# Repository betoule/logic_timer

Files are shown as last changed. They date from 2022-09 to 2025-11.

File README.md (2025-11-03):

# Arduino Code to record precise TTL pulse timing for several lines in parallel over long duration

The provided code monitors TTL lines and put a 32 bit timestamp each
time a front is detected on one of the lines. The 32 bit timestamps,
provides more than 2000 seconds of monitoring with 0.5μs resolution,
and is provided by the microcontroller internal clock. A one byte flag
identifies the TTL line corresponding to each event.

The code is written for Atmega 2560 (monitoring up to 6 lines in
parallel) and 326P (up to 2 lines) and has been tested on Arduino Mega
2560 and Arduino Nano boards. The Arduino API being bypassed in
several places to solve performance and timing issues, port to other
microcontrollers may require a bit of work.

## Installation

The code comes in two parts: a firmware for the microcontroller unit
(MCU) and a python API handling the custom communication with the
MCU. Both live in the same repository than can be retrieve from github
with:

```
git clone https://github.com/betoule/logic_timer
```

### MCU code

The MCU code no longer requires the Arduino IDE. It can be compiled
and flashed using the regular avr suite.

+ Install everything needed with:
```
sudo apt install gcc-avr avr-libc avrdude make
```

+ Adjust the port and PORT, MCU, BAUD and PROGRAMMER entries in the
Makefile according to your board. The two supported chips are the
atmega328P and the mega2560 (default).

+ Connect the board, compile and upload the firmware with:
```
make
make flash
```

### Python API

Installation of the python API using pip is obtained as:

```
pip install .
```

## Usage

Connect the TTL and ground lines to the corresponding external
interrupt pins and ground pins on the Arduino board. The
correspondence between line identifiers and board pins is given for
the two implemented boards in the following table:

| Line Id | Flag   | Interrupt 2560 | Arduino Mega pin | Interrupt 326P | Arduino Nano pin |
|---------|--------|----------------|------------------|----------------|------------------|
| 0       | 1 << 0 | INT4           | 2                | INT0           | D2               |
| 1       | 1 << 1 | INT5           | 3                | INT1           | D3               |
| 2       | 1 << 2 | INT3           | 18               |                |                  |
| 3       | 1 << 3 | INT0           | 21               |                |                  |
| 4       | 1 << 4 | INT1           | 20               |                |                  |
| 5       | 1 << 5 | INT2           | 19               |                |                  |

The following picture displays a 3 lines implementation using an
Arduino Mega.
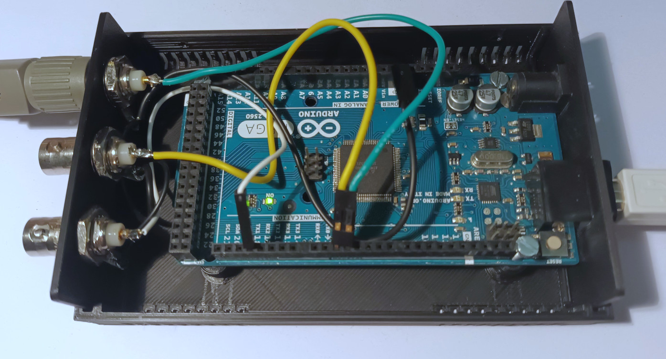
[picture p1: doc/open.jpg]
Lid open


STL files for the box are available in the 3D\_printed\_box
directory. Custom enclosure can easily been obtained with the
[ultimate box maker](https://www.thingiverse.com/thing:1264391).

Assuming that the path to the serial device corresponding to the
arduino is /dev/ttyACM0, the following command will trigger a 20 second
record of the rising edges of pin 2 and 3 and of the falling edge
of pin 18 and store the result to timing.npy: 

```
logic-timer -t /dev/ttyACM0 -d 20 -l 0r 1r 2f -o timing.npy
```

The result is a numpy record array with one entry for each detected
front and two columns *time* and *pinstate*. The timestamp in column
*time* is a 32 bit integer counting since the start of the record with
a resolution of 0.5μs. The 8 bit flag in column *pinstate* indicates
which line triggered the record according to the correspondence table
above. The record ends with a special entry whose *pinstate* value is
255. The corresponding timestamp gives the exact duration of the
monitoring.

As an example, the code below analyses a 20s record with a 1kHz square
wave in input 1. The plot displays the measured interval between
successive pulses. The rms of the measurements is 0.16 μs and peak to
peak deviation is 6 μs (see section Limitations for a discussion on
the timing accuracy).

```python
import numpy as np
import matplotlib.pyplot as plt
record = np.load('timing.npy')
t = record['time'][record['pinstate'] == 2]
t = t * 0.5e-6 # Convert timing in seconds
plt.plot(t[1:] - t[:-1], 'o')
plt.ylabel('Measured interval [s]')
plt.xlabel('Pulse number')
plt.tight_layout()
plt.savefig('doc/interval_accuracy.png')
```
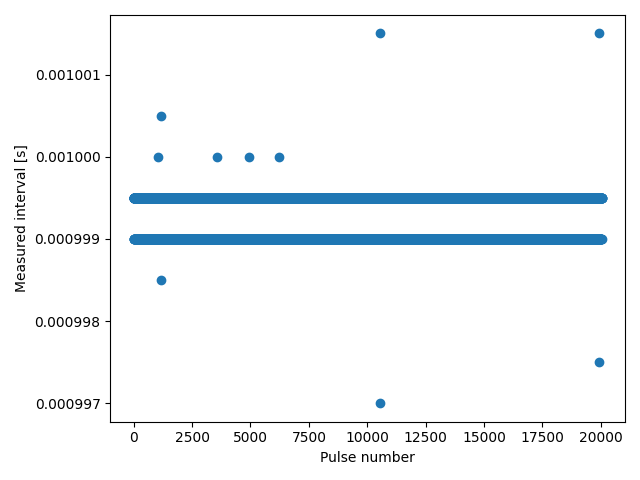
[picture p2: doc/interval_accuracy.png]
interval accuracy


## Limitations

+ Use case: The code is intended to record events occurring at random
  times. As such, it generates 5 bytes of data per detected pulses (4
  bytes for timing and 1 byte for line identification). It can only be
  used for timing events occurring with moderate frequency in
  average. It is not suited to record digital communications on a
  regular clock.

+ Handling of synchronous events: The interrupt handling routine takes
  about 5 μs to complete (82 instructions). Simultaneous events will
  therefore be reported as separated by at least 5 μs and ordered by
  the interrupt priority. This sets the worst case scenario for the
  timing precision. For non conflicting events the timing precision is
  limited by the clock resolution of 500 ns.
  
* Events in close succession: For the same reason, the second of two
  events occurring on the same line at an interval smaller than 5μs
  will be ignored. With some work to rewrite the interrupt handling
  routine in assembler, the dead time could probably be brought down
  to 2μs. If you think it could be useful, feel free to submit an
  issue. For the record, the timestamps is currently attributed 2.1μs
  after the edge detection.

+ Average frequency: The maximal average frequency of events is
  limited by the bandwidth of the serial communication. The data is
  send encapsulated in packets of 8 bytes fed to a 256 bytes buffer
  (32 events). The buffer is emptied as fast as possible through the
  serial link. 1Mbps communication have been found to be reliable for
  the tested boards so that the theoretical maximum for the event
  frequency in a sliding window of 32 events is about 15kevents/s. In
  practice overflowing the buffer will possibly result in crashing the
  microcode beyond recovery, therefore a solid margin should be
  considered so that this cannot occur.

+ Time scale accuracy: Oscillating frequencies of the ceramic
  resonators (CSTCE16M0V53-R0) clocking the Arduino Mega boards are
  only accurate at the ~10⁻³ level. The resulting inaccuracy in the
  clock scale does not matter when the device is solely used to
  provide synchronization between the different lines. However
  comparison to external clocks are likely to be affected by the error
  in the MCU clock calibration and temperature shift. For applications
  requiring external references, the simplest work-around is to add
  the external reference as an additional line. It might be
  interesting to add functionalities to calibrate the MCU clock so
  that timestamps can be accurately converted to seconds for
  application where the time scale matters. Reaching acceptable
  accuracy would however likely require additional hardware to monitor
  the MCU temperature, or replacement of the ceramic oscillator with a
  temp controlled Xtal oscillator (TCXO such as DS3231). Nano boards
  ship with a quartz resonator from which better accuracy might be
  expected. Unfortunately the 326 only features 2 external interrupts.

# How to cite



By releasing logic_timer as an open source tool we want to foster open
science and enable everyone to use it in their research free of
charge. If it proves useful and you would like to acknowledge the
author in your publication, you can cite the DOI (see badge above). Do
not hesitate to send an email for support and/or collaboration.

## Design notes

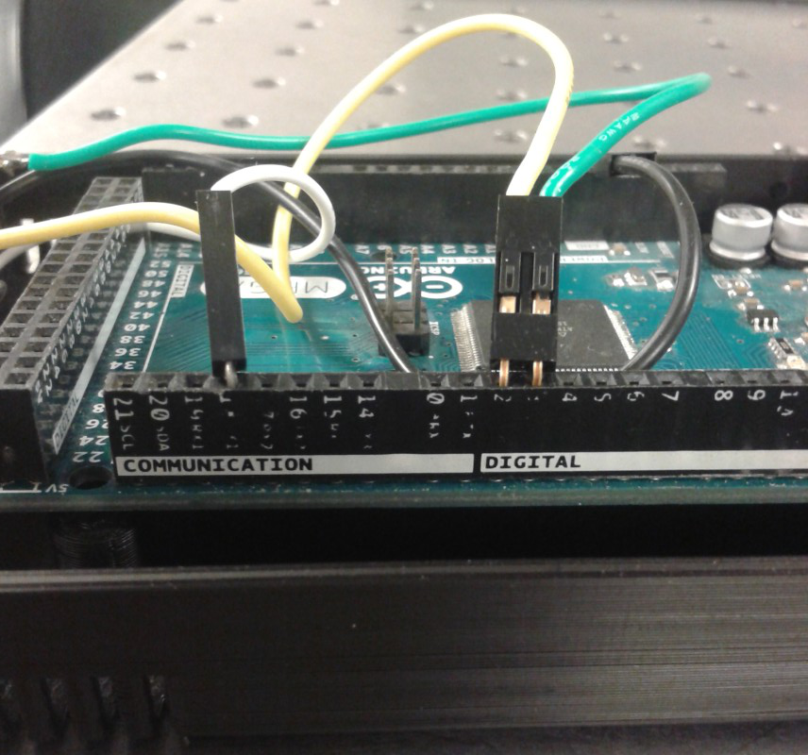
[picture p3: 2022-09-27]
doc/pins.jpg

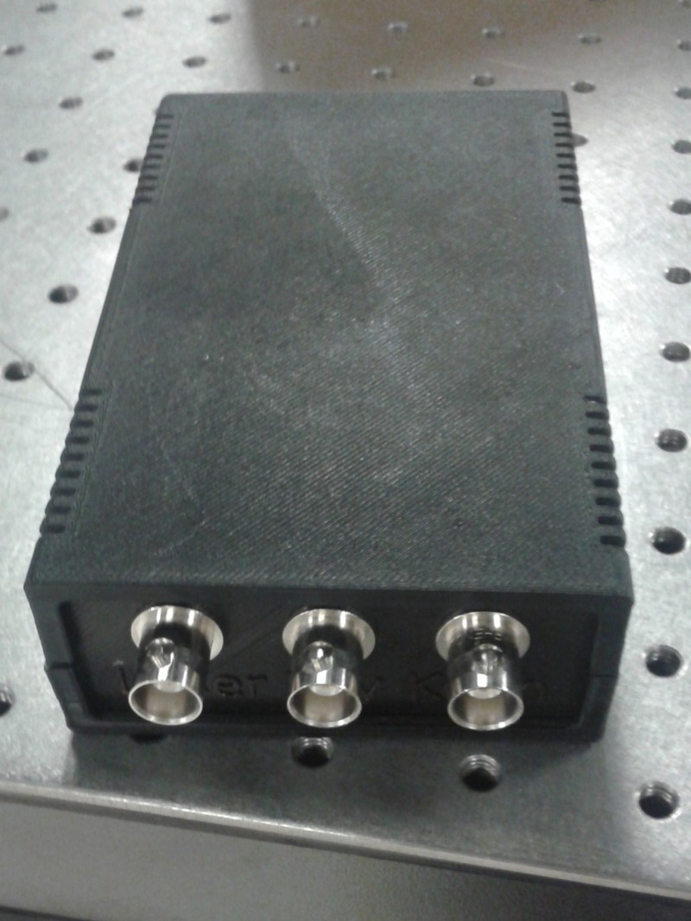
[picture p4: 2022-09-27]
doc/front.jpg

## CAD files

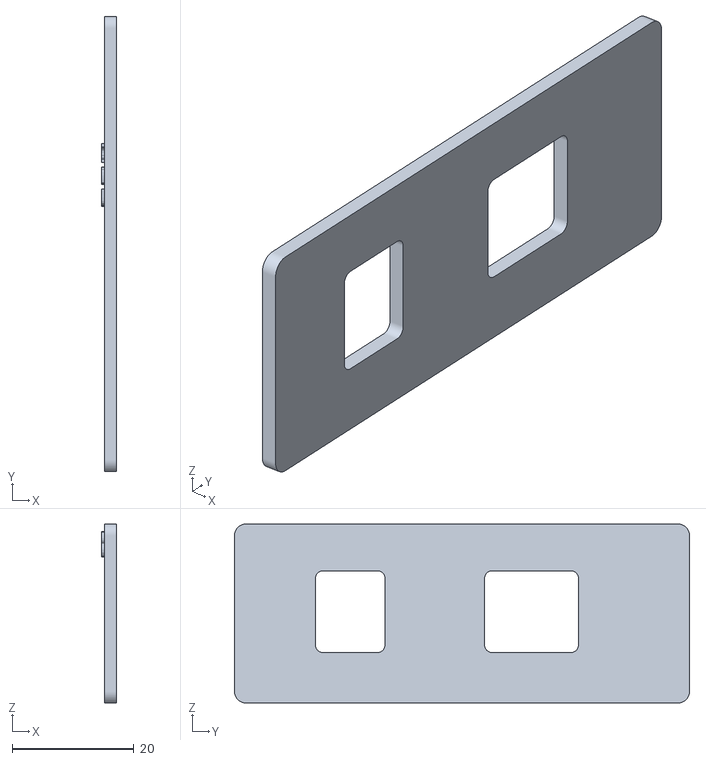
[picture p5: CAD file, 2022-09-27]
3D_printed_box/back_pannel.stl
2.50 x 74.7 x 29.4

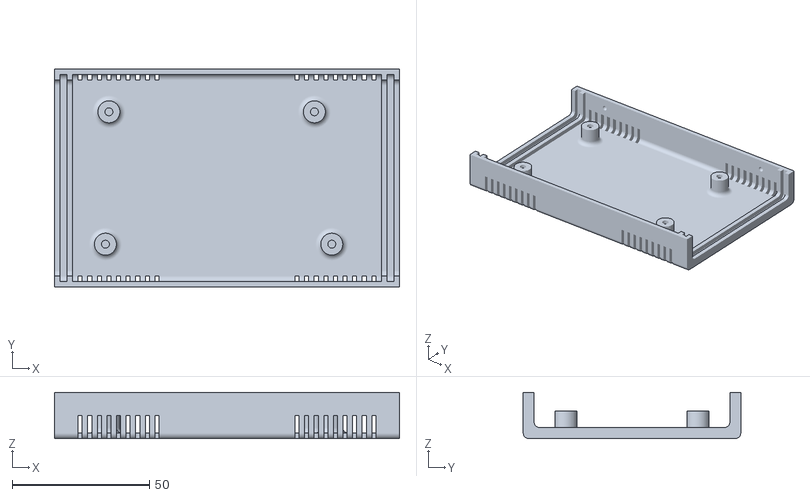
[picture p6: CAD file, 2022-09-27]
3D_printed_box/bottom.stl
125.8 x 79.3 x 16.8

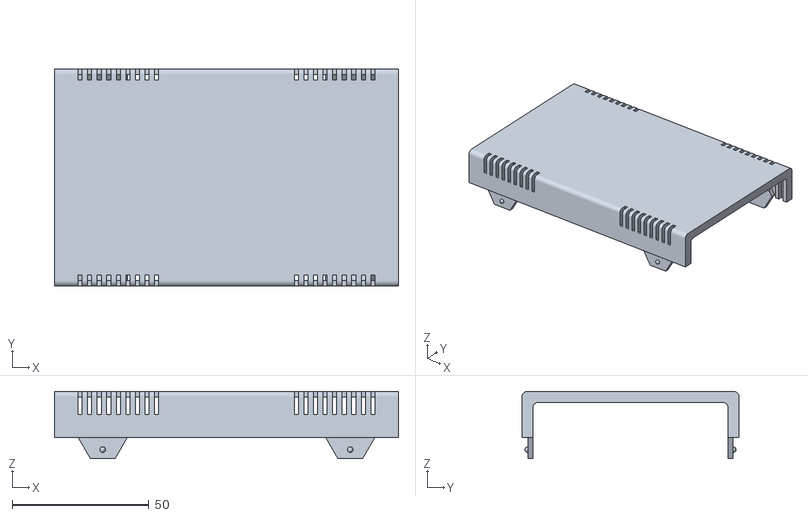
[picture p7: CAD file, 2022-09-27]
3D_printed_box/top.stl
125.8 x 79.3 x 24.6

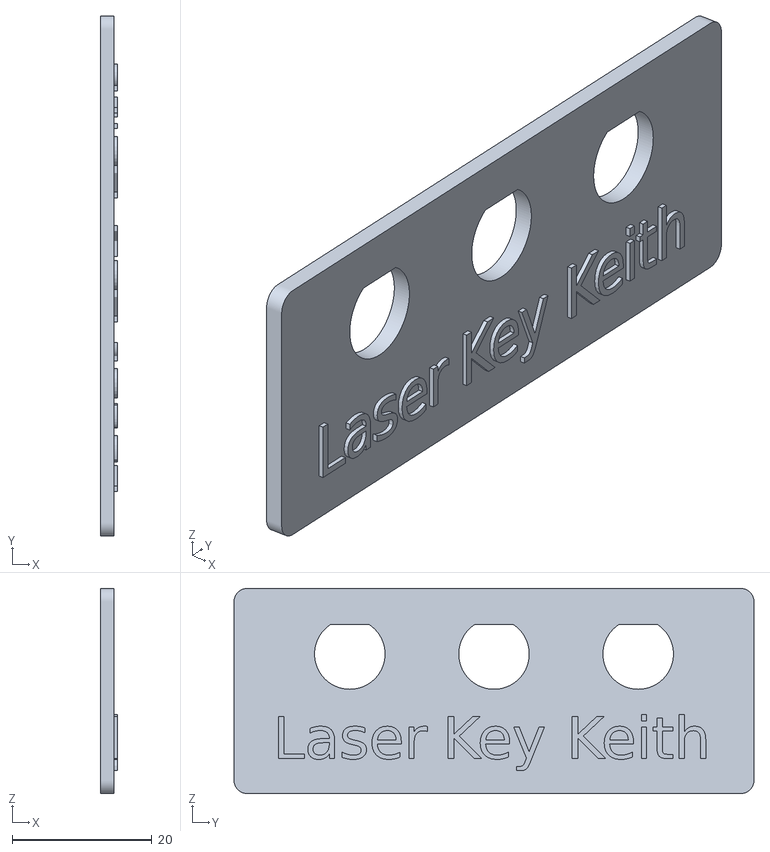
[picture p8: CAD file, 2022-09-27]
3D_printed_box/front_pannel_3bnc.stl
2.50 x 74.5 x 29.4

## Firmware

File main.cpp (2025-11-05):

// Copyright 2022 Marc Betoule
// 
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
//#include <Arduino.h>
#define F_CPU 16000000UL
#include <avr/io.h>
#include <avr/interrupt.h>
//#include <cstdio>
#include "bincoms.h"
#include <avr/eeprom.h>

extern struct Com client;

// Macros to start and stop the 16-bit timer
#define STOP_TIMER TCCR1B = 0b00000000
#define START_TIMER TCCR1B = 0b00000010
// External interupt lines
#define ENABLEINT EIMSK |= enabled_lines
#define DISABLEINT EIMSK &= ~enabled_lines
#define CLEARINT EIFR |= enabled_lines
#define CLEAR_TINT TIFR1 = _BV(OCF1A)

#if defined(ARDUINO_AVR_MEGA2560)
#define NLINES 6
const uint8_t line_correspondence[] = {4, 5, 3, 0, 1, 2};
#elif defined(ARDUINO_AVR_PRO)
#define NLINES 2
const uint8_t line_correspondence[] = {0, 1};
#else
  #error Unsupported board selection.
#endif

/* The assembly code in the MACRO below unrolls the writing of bytes
 * in the communication buffer, taking advantage on the 256 bit
 * alignment of the buffer to save time. It is roughly equivalent to:
 * client.write_buffer[client.we++] = 'b';
 * client.write_buffer[client.we++] = 0x00;
 * client.write_buffer[client.we++] = 5;
 * client.write_buffer[client.we++] = ((char*) &timeLB)[0];
 * client.write_buffer[client.we++] = ((char*) &timeLB)[1];
 * client.write_buffer[client.we++] = ((char*) &timeHB)[0];
 * client.write_buffer[client.we++] = ((char*) &timeHB)[1];
 * client.write_buffer[client.we++] = line;
 */
#define INTERRUPT_HANDLER(line)                                    \
  uint16_t timeLB = TCNT1;					   \
  if ((TIFR1 & 0b1) && (timeLB < 10)){				   \
    timeHB++;							   \
    TIFR1 |= _BV(TOV1);						   \
  }								   \
  volatile uint8_t * val_pointer = client.write_buffer + client.we;\
  asm volatile("ldi r24, 0x62" "\n\t"				   \
	       "st %a1, r24" "\n\t"				   \
	       "ldi r24, 0x00" "\n\t"				   \
	       "inc %A1" "\n\t"					   \
	       "st %a1, r24" "\n\t"				   \
	       "ldi r24, 0x05" "\n\t"				   \
	       "inc %A1" "\n\t"					   \
	       "st %a1, r24" "\n\t"				   \
	       "inc %A1" "\n\t"					   \
	       "st %a1, %A0" "\n\t"				   \
	       "inc %A1" "\n\t"					   \
	       "st %a1, %B0" "\n\t"				   \
	       "inc %A1" "\n\t"					   \
	       "st %a1, %A2" "\n\t"				   \
	       "inc %A1" "\n\t"					   \
	       "st %a1, %B2" "\n\t"				   \
	       "ldi r24, %3" "\n\t"				   \
	       "inc %A1" "\n\t"					   \
	       "st %a1, r24" "\n\t"				   \
	       : 						   \
	       : "r" (timeLB),					   \
		 "e" (val_pointer),				   \
		 "r" (timeHB),					   \
		 "I" (line)                                        \
	       :"r24"						   \
	       );						   \
  client.we += 8;                                                  \


void start(uint8_t rb);
void enable_line(uint8_t rb);
void get_enabled_lines(uint8_t rb);
void start_timer(uint8_t rb);
void get_time(uint8_t rb);
void get_clock_calibration(uint8_t rb);
void set_clock_calibration(uint8_t rb);
void read_adc(uint8_t rb);
void read_signature_row(uint8_t rb);

uint16_t duration;
uint16_t timeHB;
uint8_t enabled_lines = 0;

const uint8_t NFUNC = 2+9;
uint8_t narg[NFUNC];
// The exposed functions
void (*func[NFUNC])(uint8_t rb) =
  {// Communication protocol
   command_count,
   get_command_names,
   // user defined
   start,
   enable_line,
   get_enabled_lines,
   start_timer,
   get_time,
   get_clock_calibration,
   set_clock_calibration,
   read_adc,
   read_signature_row,
  };

const char* command_names[NFUNC*3] =
  {"command_count", "", "B",
   "get_command_names", "BB", "s",
   // user defined
   "start", "f", "H",
   "enable_line", "Bc", "",
   "get_enabled_lines", "", "B",
   "start_timer", "", "",
   "get_time", "", "I",
   "get_clock_calibration", "", "f",
   "set_clock_calibration", "f", "",
   "read_adc", "B", "H",
   "read_signature_row", "H", "B",
  };

void enable_line(uint8_t rb){
  if (client.read_buffer[rb] >= NLINES)
    client.sndstatus(VALUE_ERROR);
  else{
    uint8_t sense_control_bit = 0;
    uint8_t int_num = line_correspondence[client.read_buffer[rb]];
    if (client.read_buffer[rb+1] == 'r')
      sense_control_bit = 0b11;
    else if (client.read_buffer[rb+1] == 'f')
      sense_control_bit = 0b10;
    else if (client.read_buffer[rb+1] == 'b')
      sense_control_bit = 0b01;
    else
      client.sndstatus(VALUE_ERROR);
    enabled_lines |= 1 << int_num;
    if (int_num < 4){
      EICRA = (EICRA & ~(0b11 << 2*int_num)) | (sense_control_bit << (2*int_num));
    }
    else{
      int_num -= 4;
      EICRB = (EICRB & ~(0b11 << 2*int_num)) | (sense_control_bit << (2*int_num)); 
    }
    client.sndstatus(STATUS_OK);
  }
}

void setup(){
  setup_bincom();

#if defined(ARDUINO_AVR_MEGA2560)
  // MEGA pin assignments
  // PORT B D and E setup
  // All pull-up inputs but for output on arduino pin 13
  DDRB   = 0b10000000;
  PORTB  = 0b01111111;
  DDRD   = 0b00000000;
  PORTD  = 0b11111111;
  DDRE   = 0b0;
  PORTE  = 0b11111111;
  //PORTE  = 0b0;
  PCMSK0 = 0b00000000;
  // Setup external interrupt rise for arduino pin 2 and 3 (PE4 and PE5)
  //PCICR |= _BV(PCIE0);
  EICRB |= _BV(ISC51) | _BV(ISC50) | _BV(ISC41) | _BV(ISC40);
  // Setup external interrupt falling for arduino pin 18 (PD3)
  EICRA |= _BV(ISC31);
  EICRA &= ~_BV(ISC30);
#elif defined(ARDUINO_AVR_PRO)
  // Pro Mini assignments
  // PORTB setup for output on arduino pin 13
  DDRB   = _BV(PB5);
  PORTB  = ~_BV(PB5);
  // PORTD PIN D2 and D3 
  PCMSK0 = 0b00000000;
  // Setup external interrupt rise for arduino pin 2 and 3 (INT0 and INT1)
  EICRA |= _BV(ISC11) | _BV(ISC10) | _BV(ISC01) | _BV(ISC00);  
#else
  #error Unsupported board selection.
#endif
  
  //SET_TIMER1_CLOCK(TIMER_CLOCK_1);
  // 16-bit TIMER1 settings
  // This timer is used to follow the clock count
  // TCCR1A: COM1A1:COM1A0:COM1B1:COM1B0:0:0:WGM11:WGM10
  // TCCR1B: ICNC1:ICES1:0:WGM13:WGM12:CS12:CS11:CS10
  // TIMSK1: 0:0:ICIE1:0:0:OCIE1B:OCIE1A:TOIE1
  // COM1A: 0b01 toggle on compare match
  // COM1B: 0b01 toggle on compare match
  // WGM: 0b0100 CTC
  // WGM: 0b0000 Normal
  // CS1: 0b000 STOP
  TCCR1A = 0b00000000;
  STOP_TIMER;
  //TCCR1B = 0b00000010;
  TIMSK1 = 0b00000001;

  // Make sure other timer are disabled
  TCCR0B = 0b0;
  TIMSK0 = 0b0;
  TCCR2B = 0b0;
  TIMSK2 = 0b0;
  EIMSK = 0b0;

  // Set global interrupt enable
  sei();
}

// Handle interrupt on arduino Pin3
#if defined(ARDUINO_AVR_MEGA2560)
ISR(INT5_vect){
#elif defined(ARDUINO_AVR_PRO)
ISR(INT1_vect){  
#endif
  INTERRUPT_HANDLER(0x02)
}

// Handle interrupt on arduino pin2
#if defined(ARDUINO_AVR_MEGA2560)
ISR(INT4_vect){
#elif defined(ARDUINO_AVR_PRO)
ISR(INT0_vect){
#endif
  INTERRUPT_HANDLER(0x01)
}

#if defined(ARDUINO_AVR_MEGA2560)
// Handle interrupt on arduino pin 18
ISR(INT3_vect){
  INTERRUPT_HANDLER(0x04)
}
// Handle interrupt on arduino pin 21
ISR(INT0_vect){
  INTERRUPT_HANDLER(0b1000)
}
// Handle interrupt on arduino pin 20
ISR(INT1_vect){
  INTERRUPT_HANDLER(0b10000)
}
// Handle interrupt on arduino pin 19
ISR(INT2_vect){
  INTERRUPT_HANDLER(0b100000)
}

#endif
// Update high bytes of the timer counter
ISR(TIMER1_OVF_vect){
  timeHB++;
}

void start_timer(uint8_t rb){
  /* Start the timer execution without program
    (Usually used for clock calibration purpose)
   */
  // Disable interrupts
  DISABLEINT;
  // Reset the timer
  timeHB=0;
  TCNT1=0;
  CLEAR_TINT;
  // Enable timer overflow but not the other instructions
  TIMSK1 = 0b00000001;
  START_TIMER;
  client.sndstatus(STATUS_OK);
}

void get_time(uint8_t rb){
  uint32_t timestamp = timeHB;
  timestamp <<= 16;
  timestamp += TCNT1;
  client.snd((uint8_t*) &timestamp, 4, STATUS_OK);
}

void get_enabled_lines(uint8_t rb){
  client.snd((uint8_t*) &enabled_lines, 1, STATUS_OK);
}

void start(uint8_t rb){
  // We receive the duration as a floating point in seconds
  // Compute the corresponding value for the low resolution timer
  float secduration = *((float *) (client.read_buffer+rb));
  duration = secduration/0.032768; // time resolution 0.5e-6*2**16
  client.snd((uint8_t*) &duration, 2);
  // Reset the timer
  START_TIMER;
  timeHB=0;
  TCNT1=0;
  // Clear the interrupt vectors
  CLEARINT;
  // Enable interrupt handling
  ENABLEINT;
}

void stop(){
  // Disable interrupts
  DISABLEINT;
  STOP_TIMER;
  // Send the end packet
  uint16_t timeLB = TCNT1;
  client.write_buffer[client.we++] = 'b';
  client.write_buffer[client.we++] = 0x00;
  client.write_buffer[client.we++] = 5;
  client.write_buffer[client.we++] = ((char*) &timeLB)[0];
  client.write_buffer[client.we++] = ((char*) &timeLB)[1];
  client.write_buffer[client.we++] = ((char*) &timeHB)[0];
  client.write_buffer[client.we++] = ((char*) &timeHB)[1];
  client.write_buffer[client.we++] = 255;
  // Reset duration
  duration = 0;
}

void get_clock_calibration(uint8_t rb){
  float calibration_constant = eeprom_read_float((float*)0);
  //EEPROM.get(0, calibration_constant);
  client.snd((uint8_t*) &calibration_constant, 4, STATUS_OK);
}

void set_clock_calibration(uint8_t rb){
  float calibration_constant = 2e6;
  client.readn(&rb, (uint8_t*) &calibration_constant, 4);
  eeprom_write_float((float*)0, calibration_constant);
  //EEPROM.put(0, calibration_constant);
  client.sndstatus(STATUS_OK);
}


void read_adc(uint8_t rb){
  uint8_t channel = *((uint8_t *) (client.read_buffer + rb));
  // ADCSRA reference:
  // ADEN-ADSC-ADATE-ADIF-ADIE-ADPS2-ADPS1-ADPS0
  
  // Configure ADMUX: Internal 1.1V reference, right-adjusted result, select channel
  ADMUX = _BV(REFS1) | _BV(REFS0) | (channel & 0x0F);

  // Start first conversion
  ADCSRA |= (1 << ADSC);

  // Wait for conversion to complete
  while(ADCSRA & _BV(ADSC));// ADSC is cleared when conversion finishes

  // Read ADC result (read ADCL first, then ADCH)
  uint16_t result = ADCL; // Read low byte first
  result += (ADCH<<8); // Read high byte and combine
  
  client.snd((uint8_t *) &result, 2, STATUS_OK);
}

/** The mcu signature contains calibration constants for the MCU temperature sensor
 */
void read_signature_row(uint8_t rb) {
    uint8_t result;
    uint16_t address;
    client.readn(&rb, (uint8_t*) &address, 2);
    
    // Disable interrupts to ensure atomic operation
    cli();

    // Wait for any ongoing SPM/EEPROM operations to complete
    while (SPMCSR & (1 << SPMEN));

    // Set SIGRD and SPMEN to enable signature row read
    SPMCSR = (1 << SIGRD) | (1 << SPMEN);
    
    // Load the address into Z register (R31:R30) and read using LPM
    asm volatile("lpm %1, Z" "\n\t"    // Read byte from program memory at Z into result
		 : "=r" (result)        // Output: result
		 : "z" (address)   // Input: address (shifted left by 1 for word addressing)
		 );

    // Clear SPMCSR
    SPMCSR = 0;

    // Re-enable interrupts
    sei();

    client.snd(&result, 1, STATUS_OK);
}

 
int main(void) {
  setup();
  client.serve_serial();
}

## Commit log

2022-09-27 add stl files for 3D printed box
    [back_pannel.stl, bottom.stl, front_pannel_3bnc.stl, top.stl]
2022-09-28 succesful attempt to unroll the communication in assembly
2022-09-28 All the interrupt communication rewritten in assembly code
2022-11-22 try to open the serial port without reseting the arduino
2025-11-02 Get rid of the last arduino lib dependencies. The code compile and communicate but the timing does not work
2025-11-03 implement the clock calibration functionality
2025-11-05 Apply calibration to records and add a function to display

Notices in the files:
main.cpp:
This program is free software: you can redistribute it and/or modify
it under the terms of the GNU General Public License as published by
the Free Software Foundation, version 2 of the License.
